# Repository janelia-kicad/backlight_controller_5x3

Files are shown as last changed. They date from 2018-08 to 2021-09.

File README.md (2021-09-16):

- [Repository Information](#orge3a2ecc)
  - [Description](#org1a124a6)
- [Images](#orgde4a8eb)
- [Schematic](#org565d04b)
- [Gerbers](#orgdefb019)
- [Bill of Materials](#orgbfc12b0)
  - [PCB Parts](#org35e0f28)
  - [Supplemental Parts](#orgb5c14fe)
  - [Vendor Parts Lists](#org5ae73cf)
- [Supplemental Documentation](#orgd3afd80)
  - [Assembly Instructions](#orgc67ada5)
- [Manufacturing Archive](#org51454f0)

# Repository Information

-   **Name:** backlight\_controller\_5x3
-   **Version:** 1.3
-   **License:** Open-Source Hardware
-   **URL:** <https://github.com/janelia-kicad/backlight_controller_5x3>
-   **Author:** Peter Polidoro
-   **Email:** peter@polidoro.io

## Description

This board controls up to four Smart Vision backlights with IR and visible channels plus additional high and low power channel outputs.

# Images

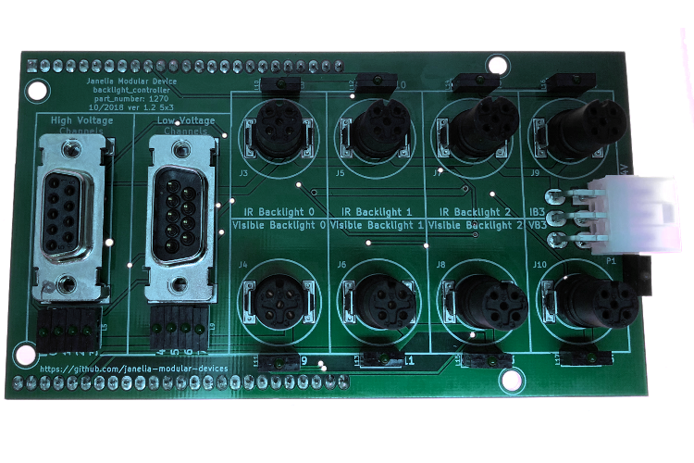
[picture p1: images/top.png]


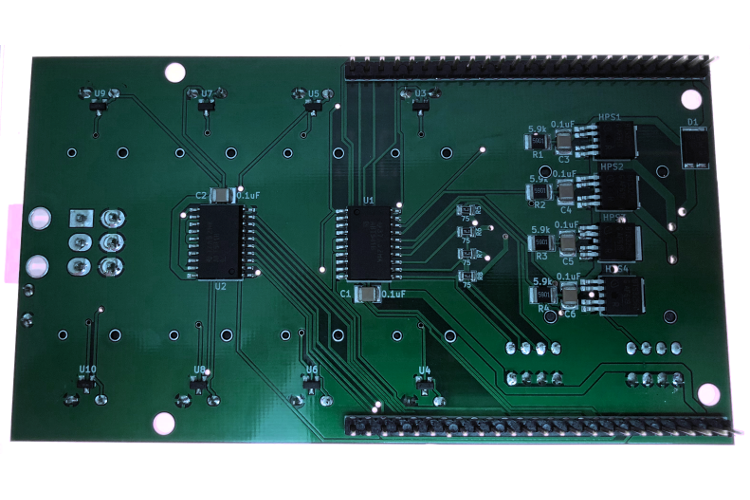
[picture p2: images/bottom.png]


# Schematic

[./schematic/backlight\_controller\_5x3.pdf](./schematic/backlight_controller_5x3.pdf)

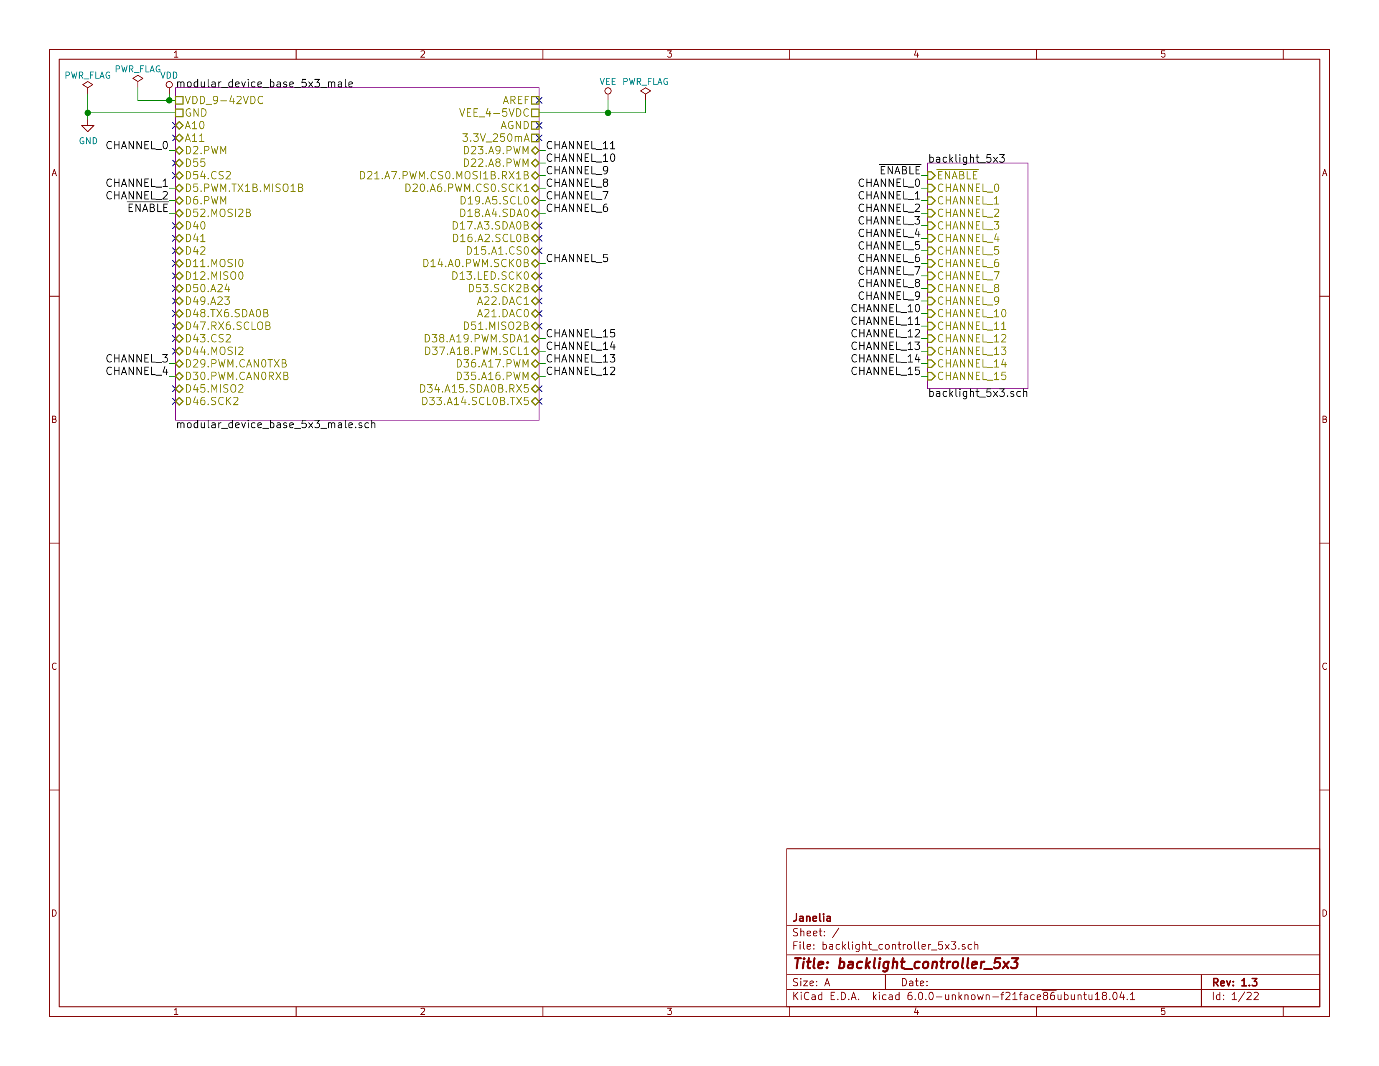
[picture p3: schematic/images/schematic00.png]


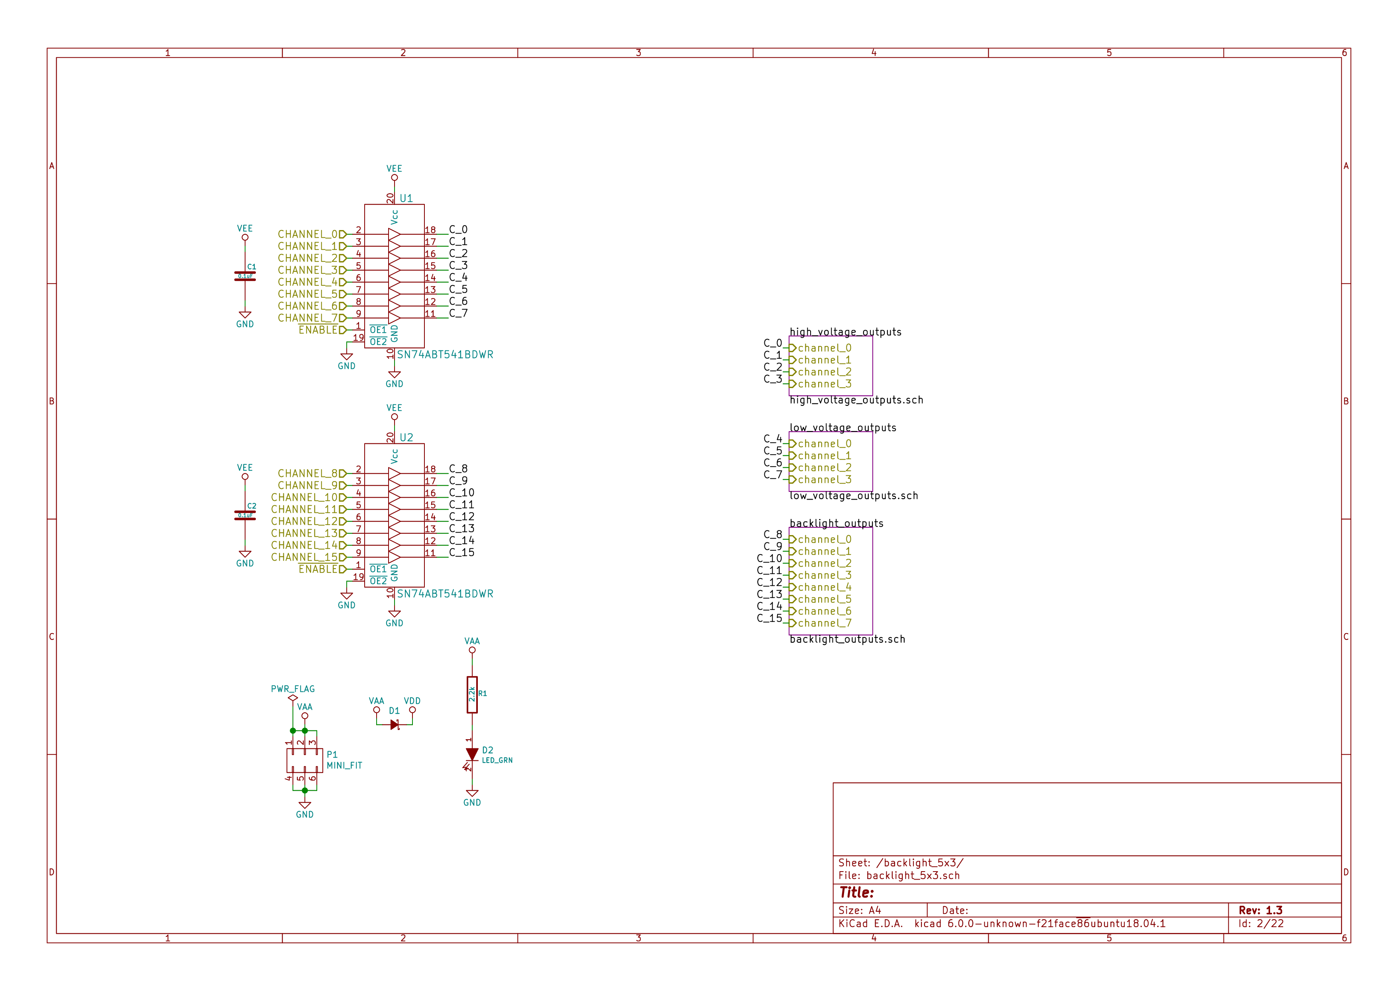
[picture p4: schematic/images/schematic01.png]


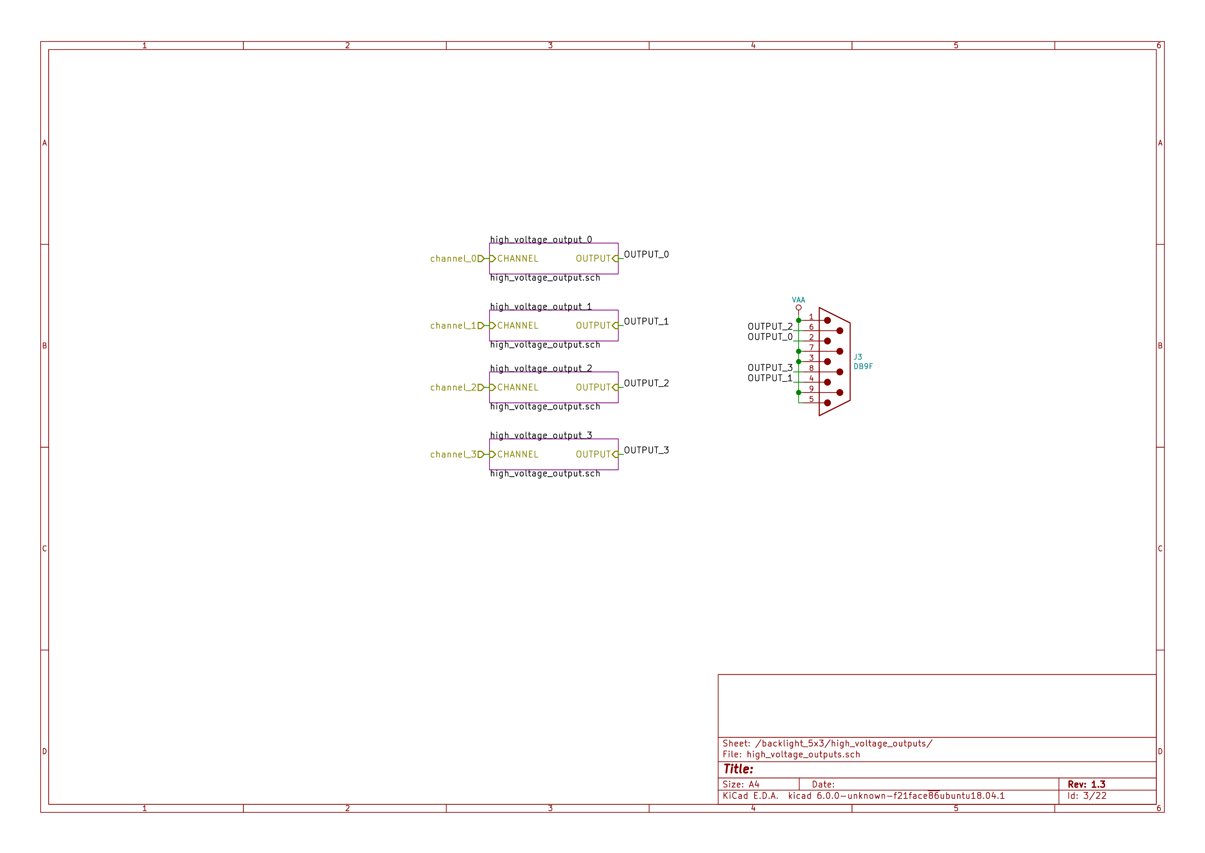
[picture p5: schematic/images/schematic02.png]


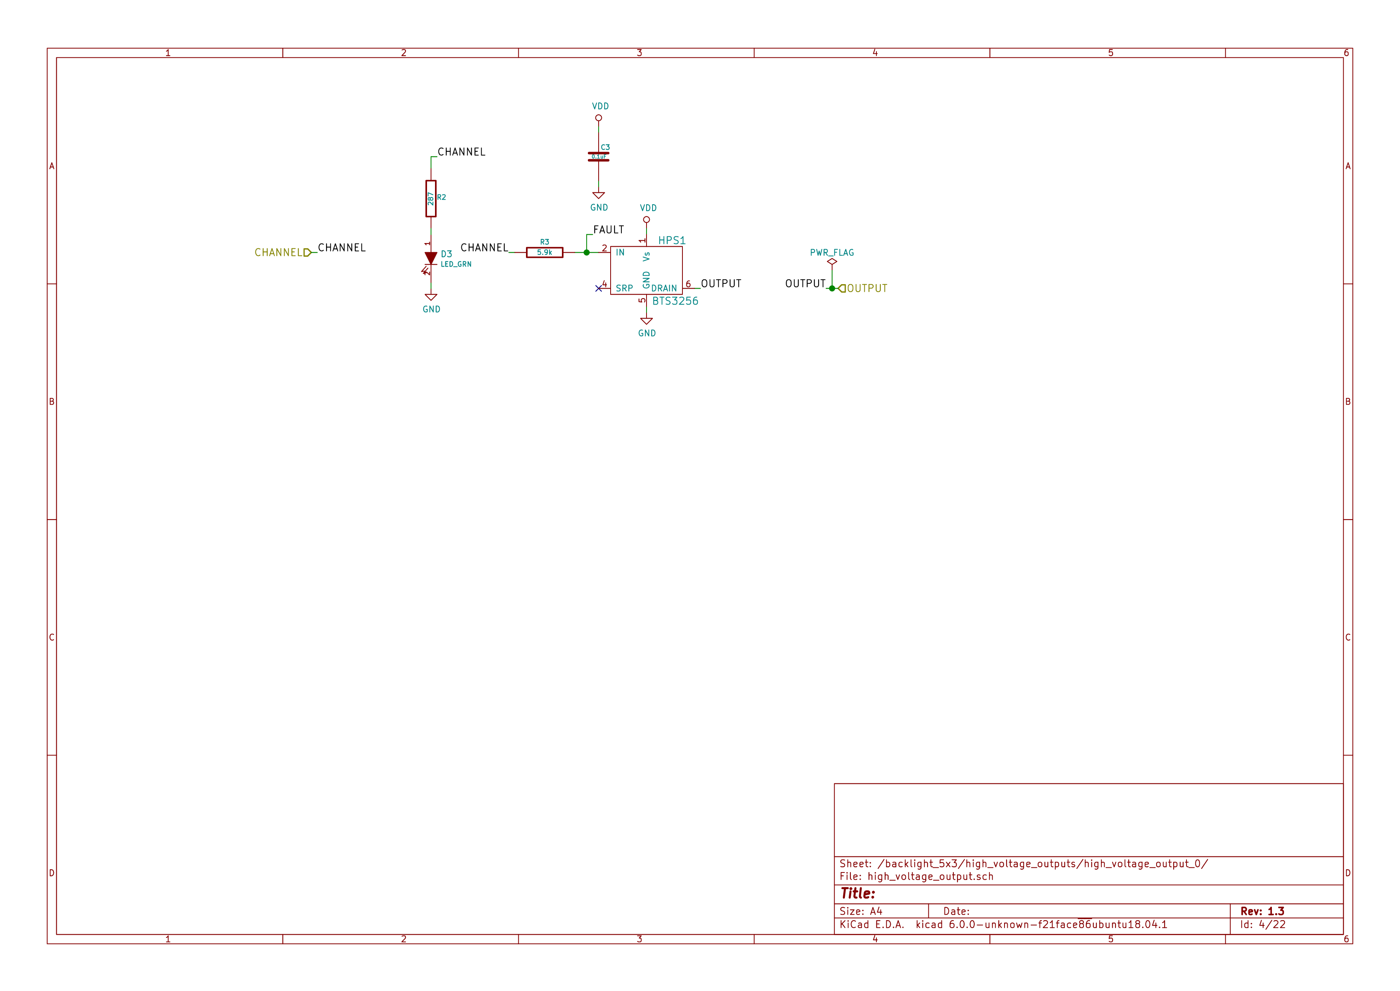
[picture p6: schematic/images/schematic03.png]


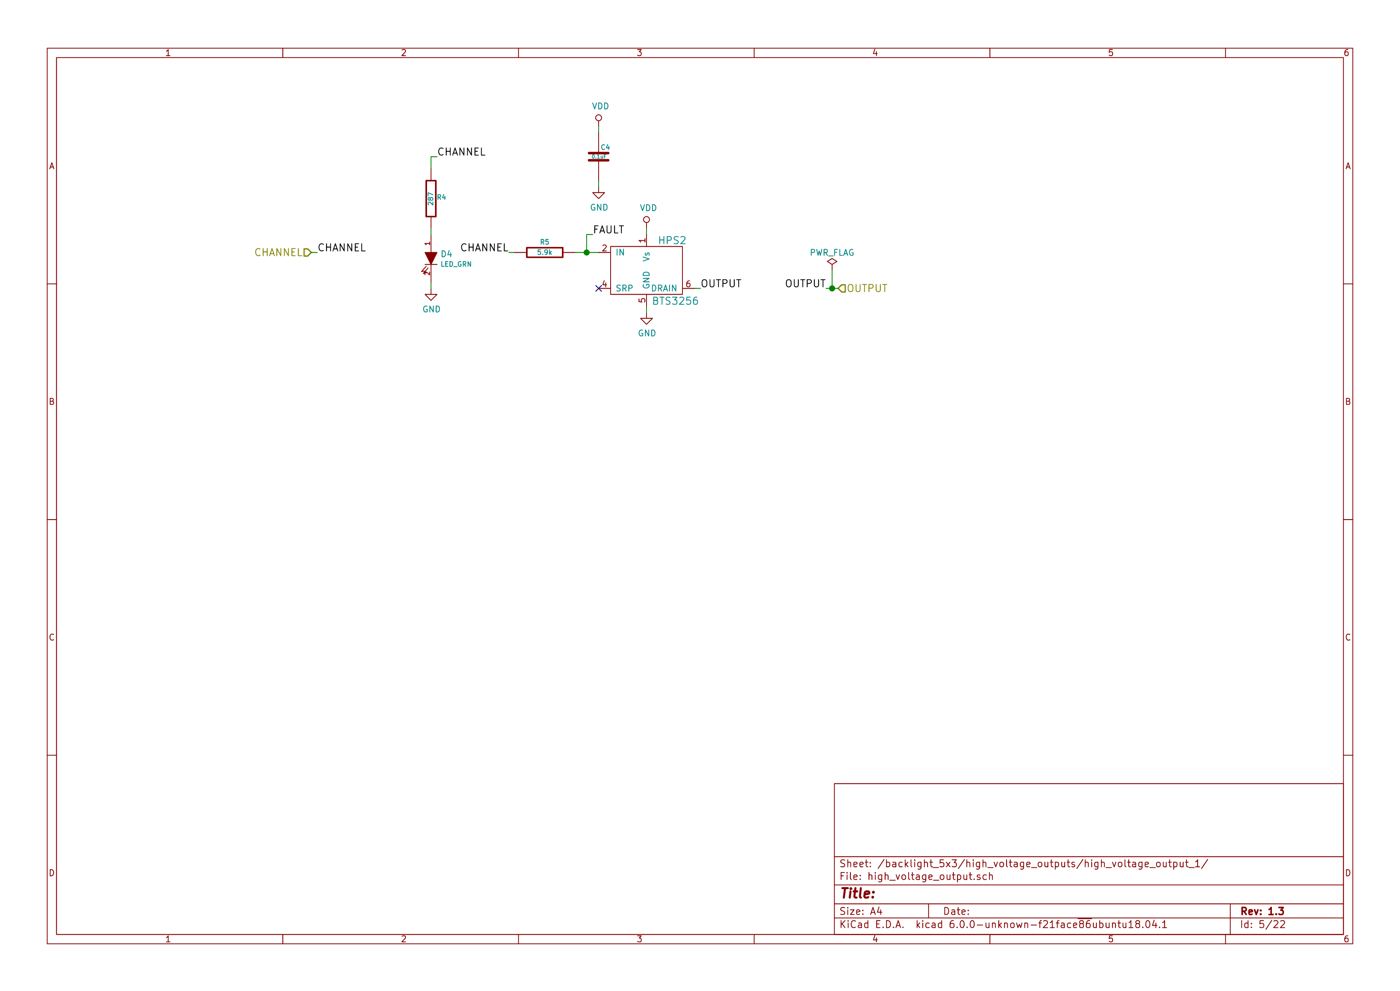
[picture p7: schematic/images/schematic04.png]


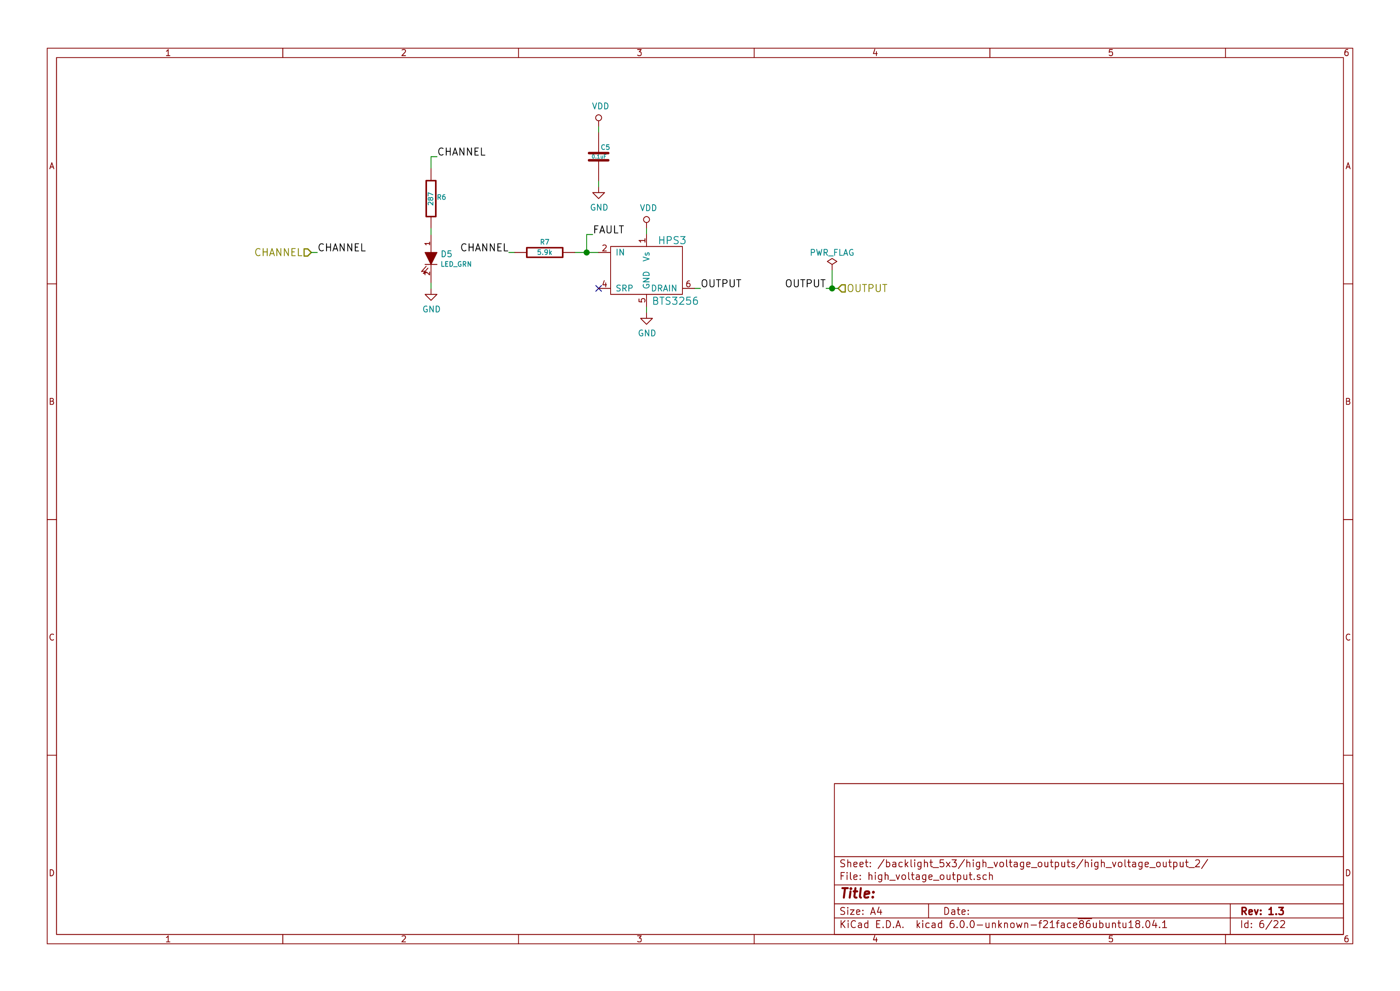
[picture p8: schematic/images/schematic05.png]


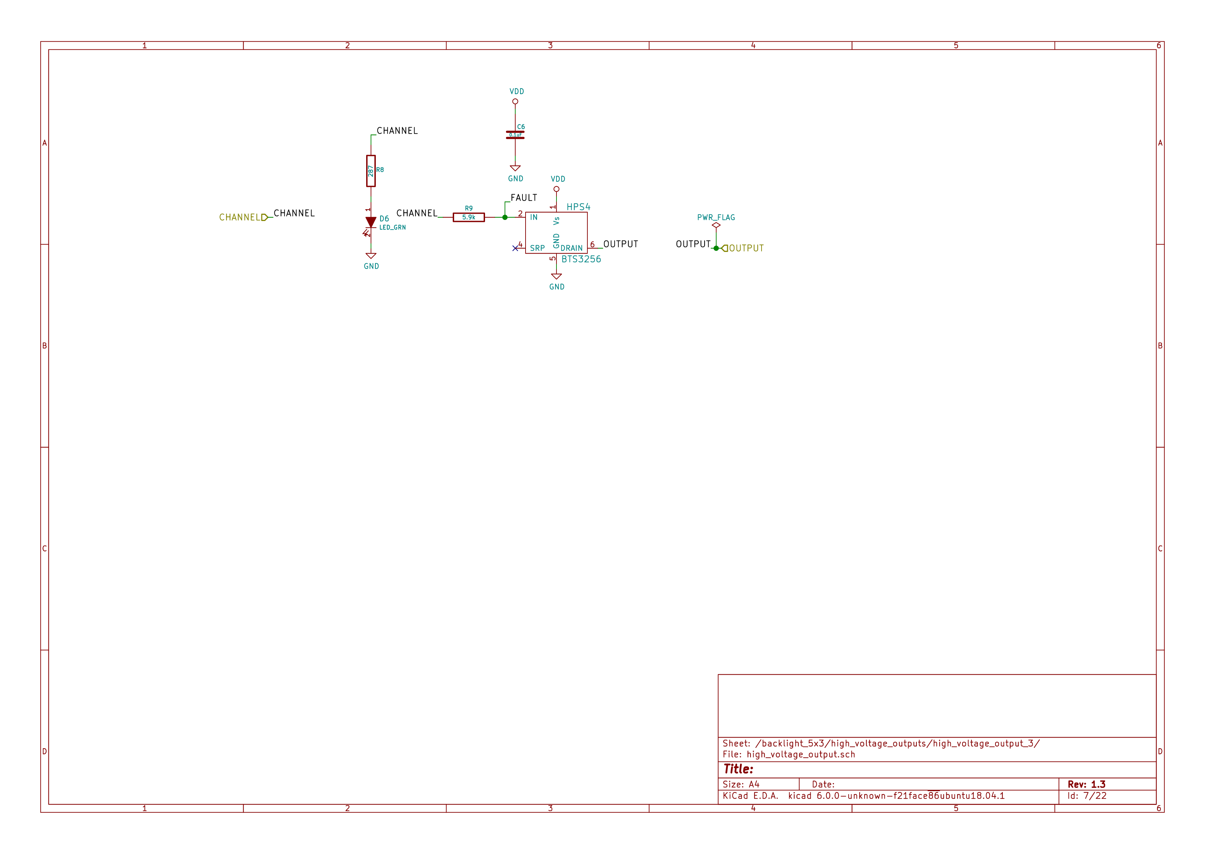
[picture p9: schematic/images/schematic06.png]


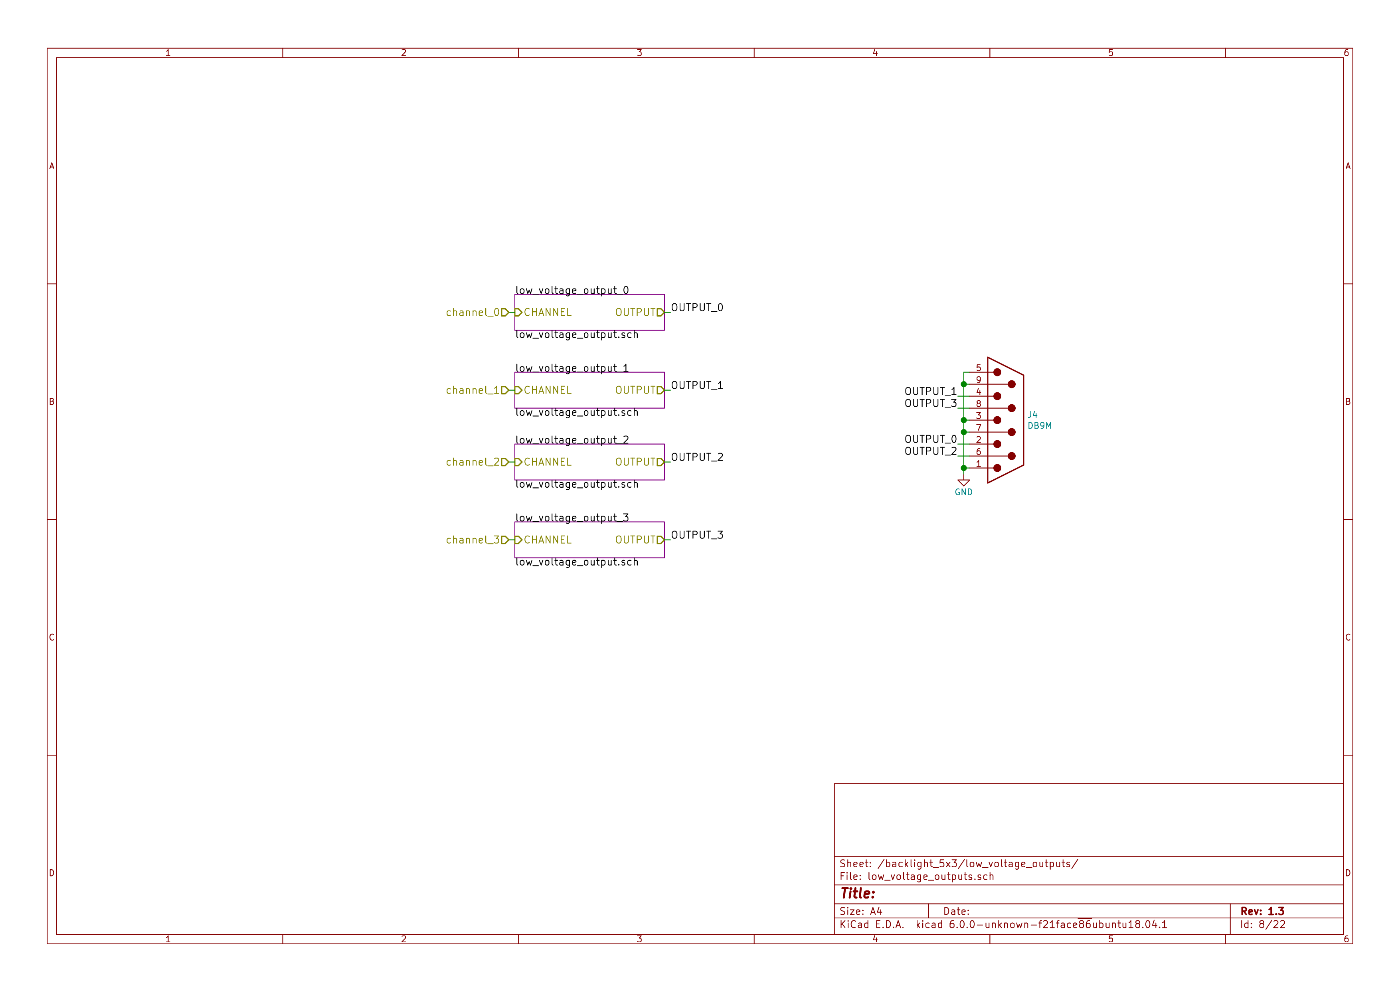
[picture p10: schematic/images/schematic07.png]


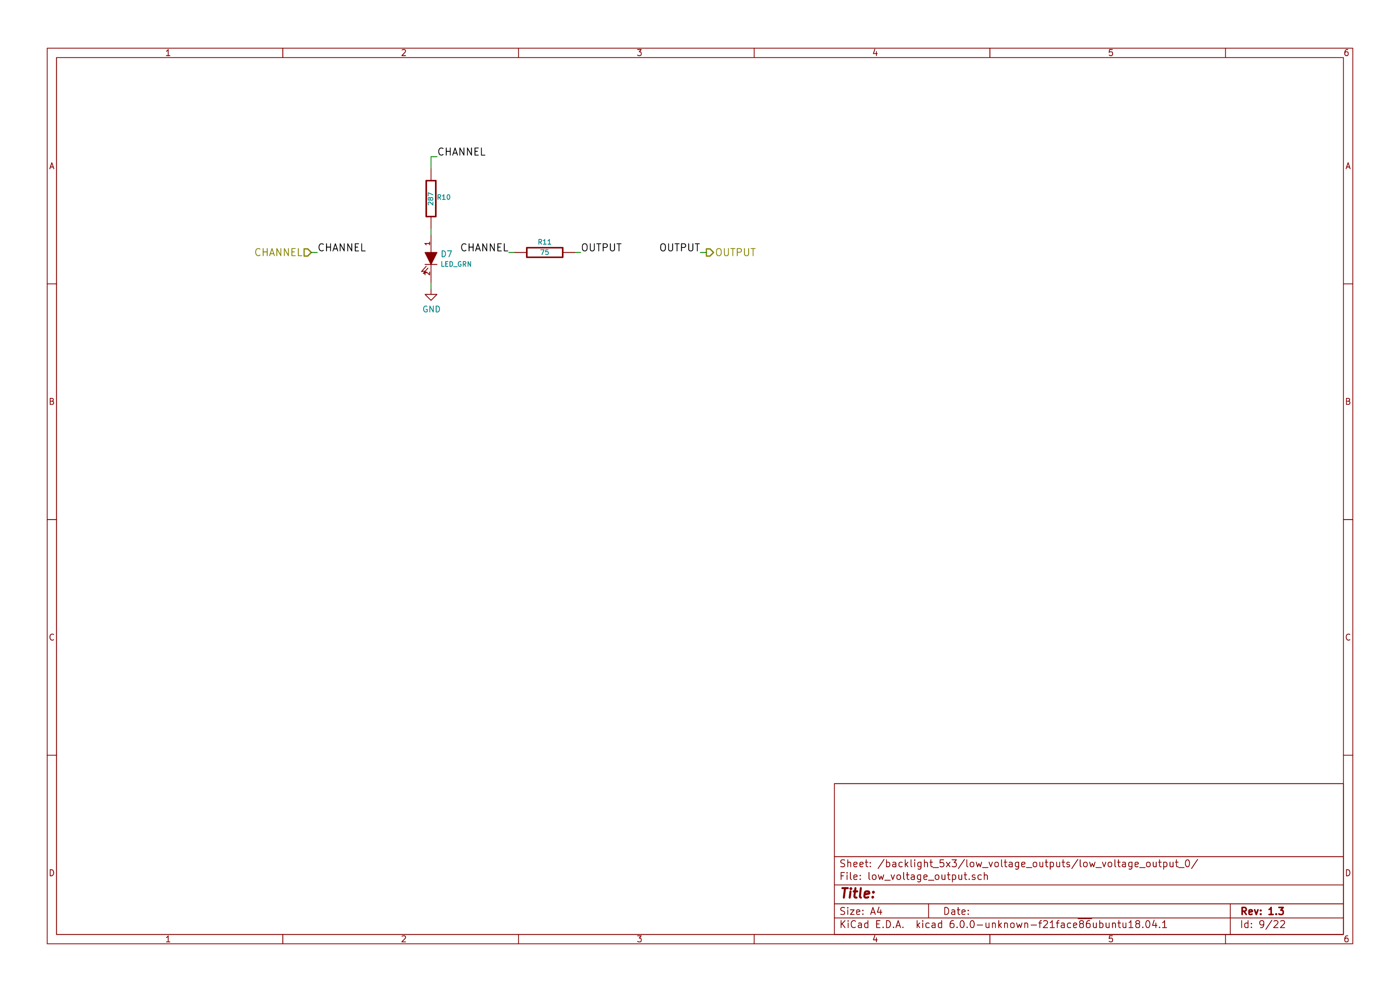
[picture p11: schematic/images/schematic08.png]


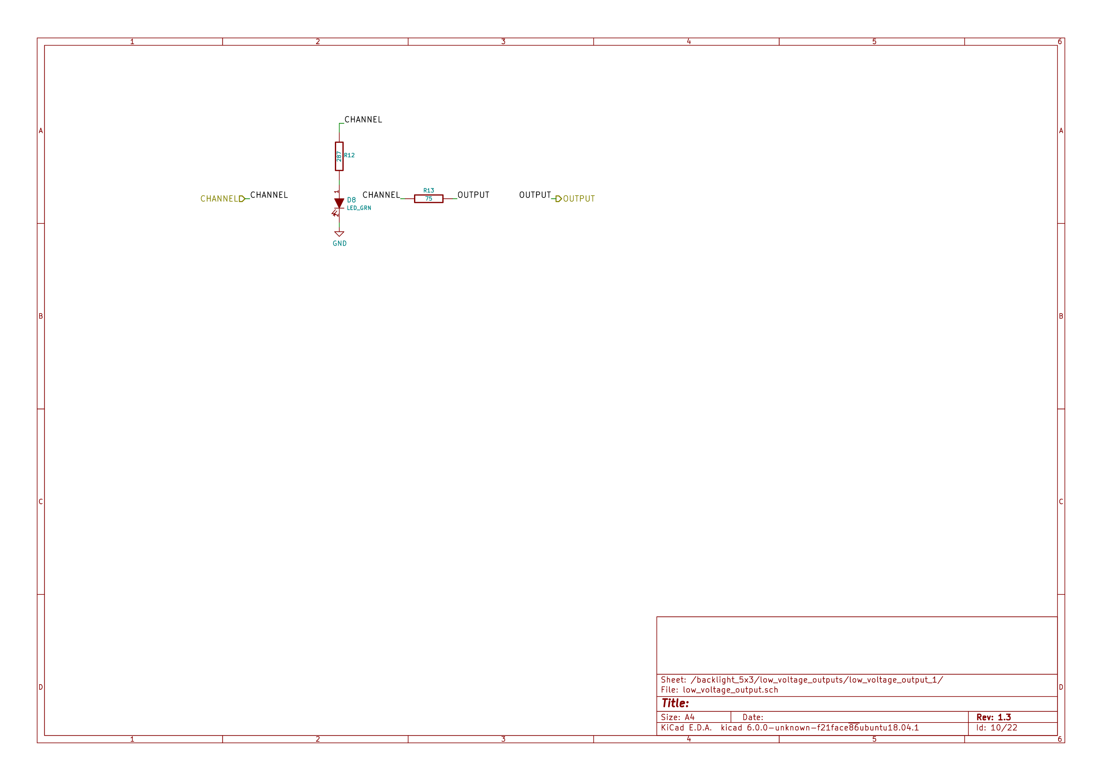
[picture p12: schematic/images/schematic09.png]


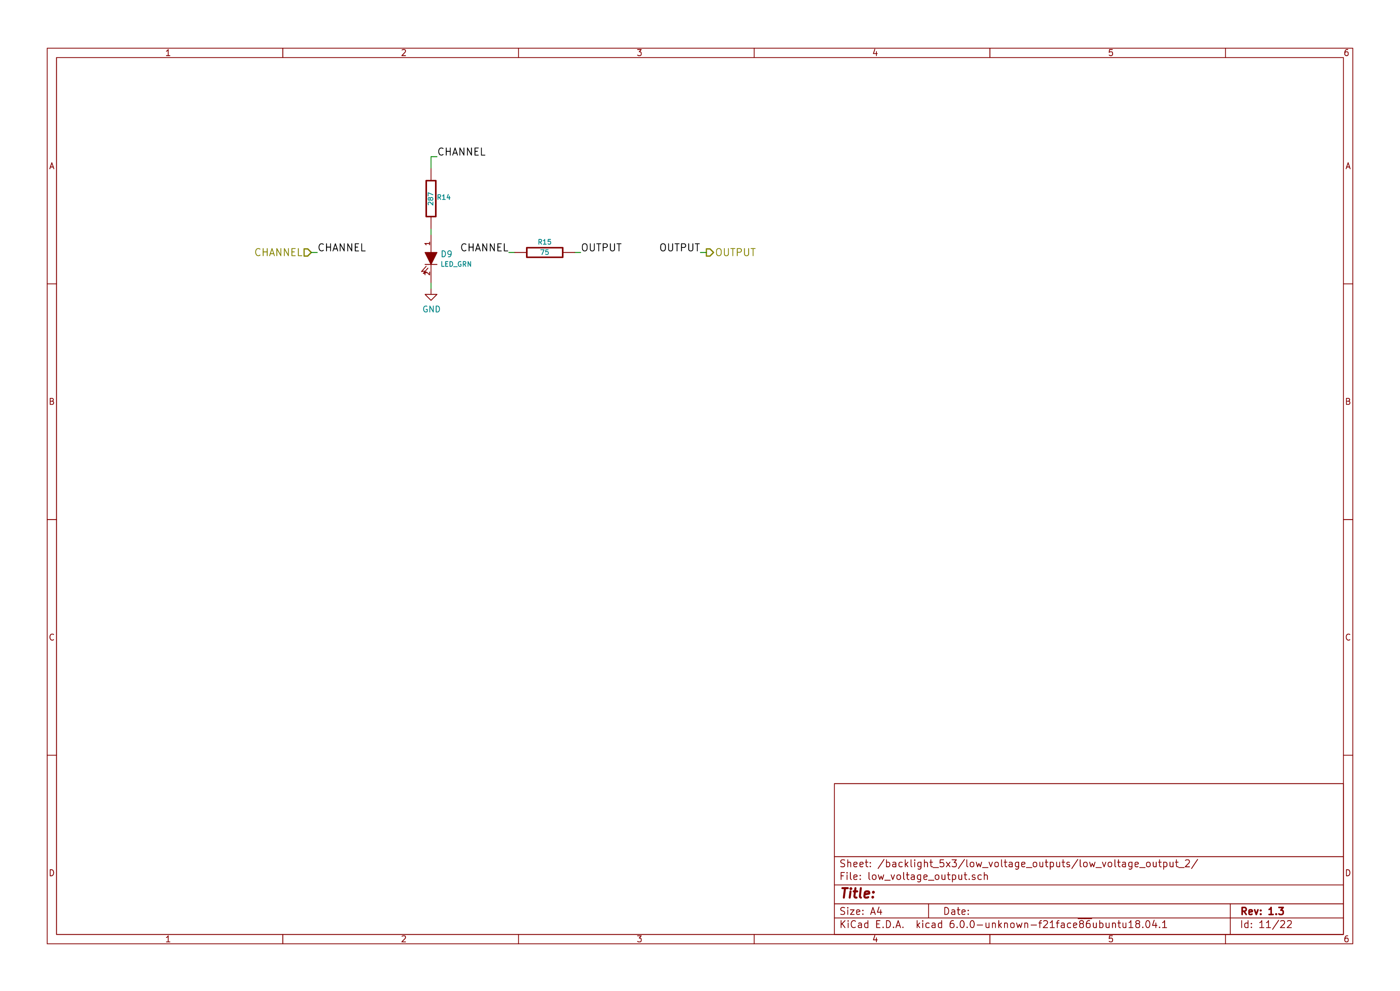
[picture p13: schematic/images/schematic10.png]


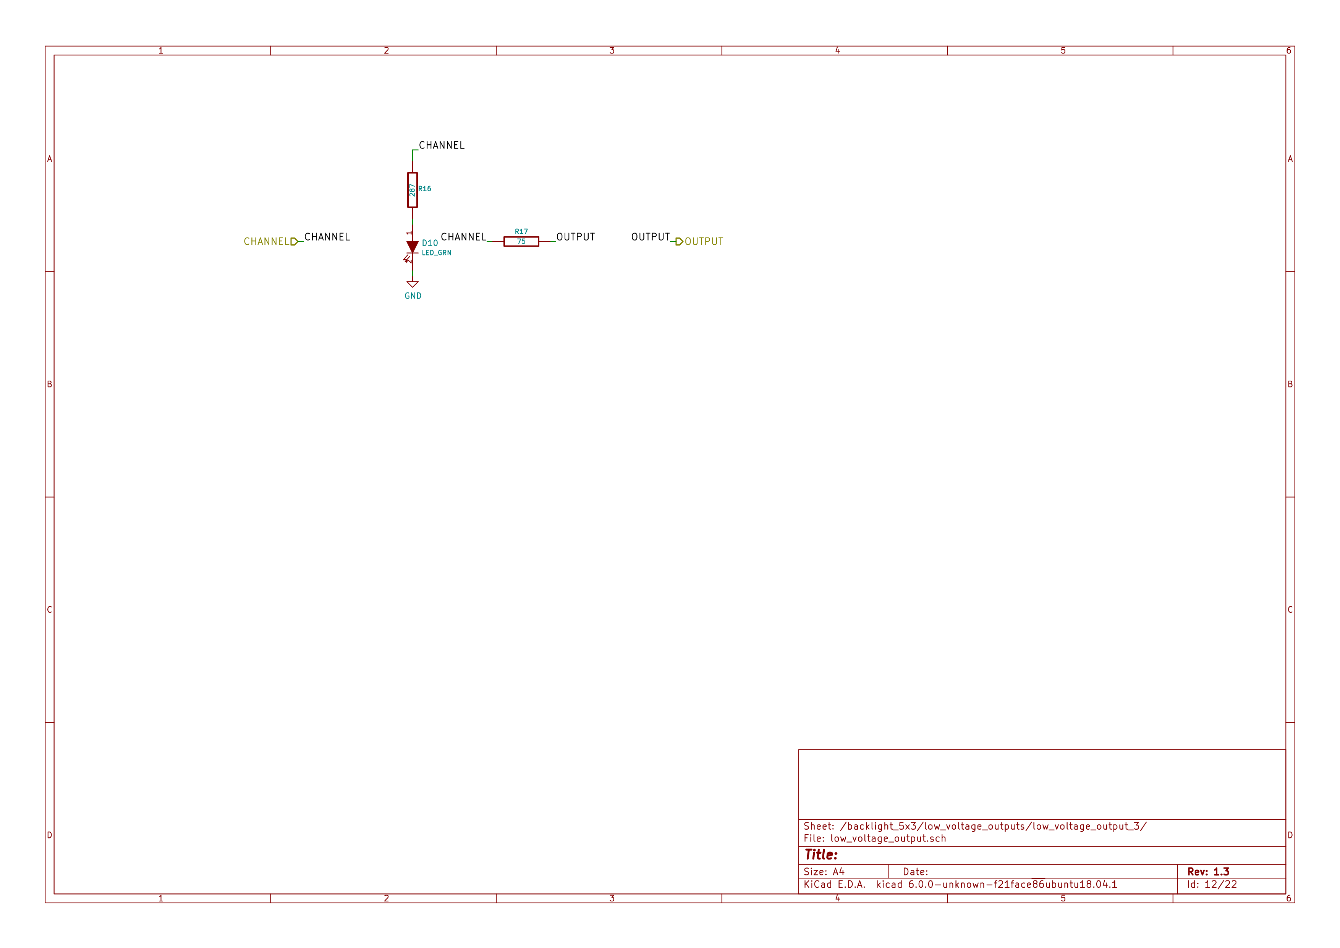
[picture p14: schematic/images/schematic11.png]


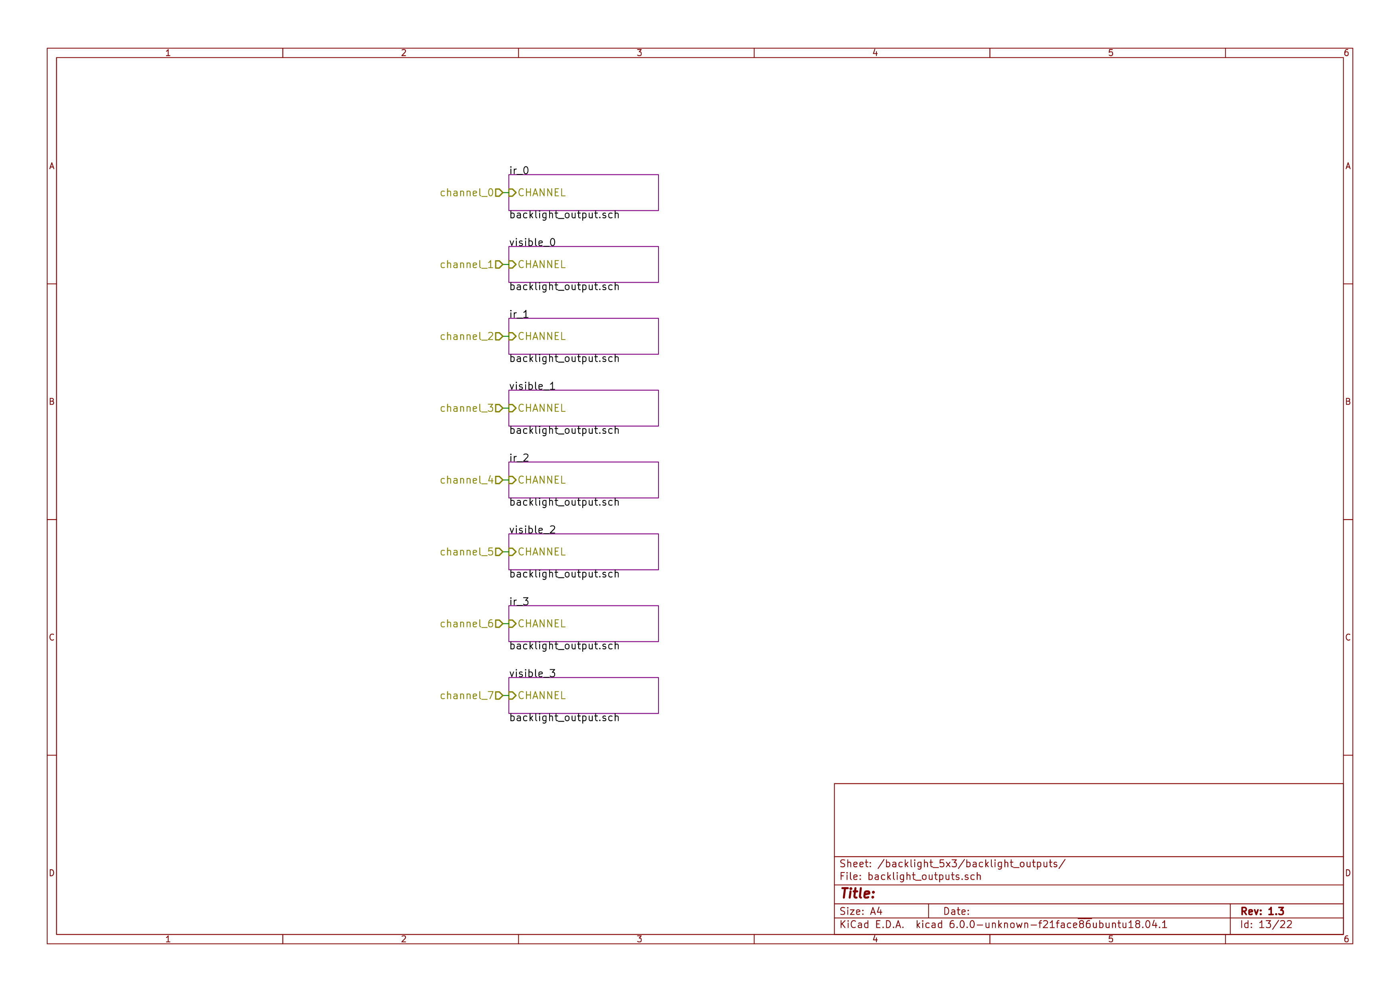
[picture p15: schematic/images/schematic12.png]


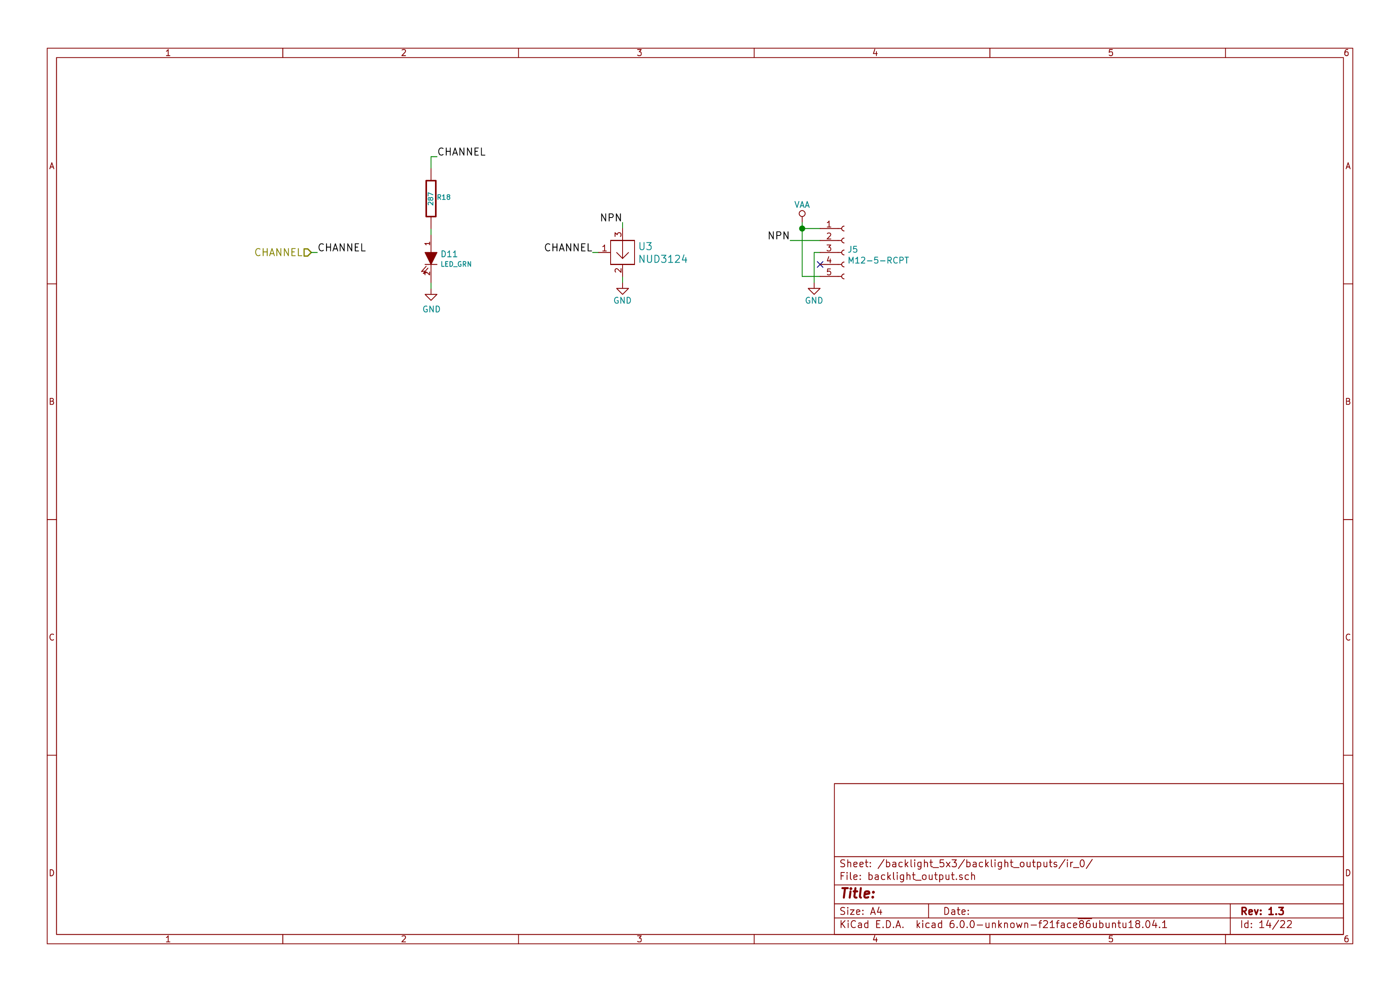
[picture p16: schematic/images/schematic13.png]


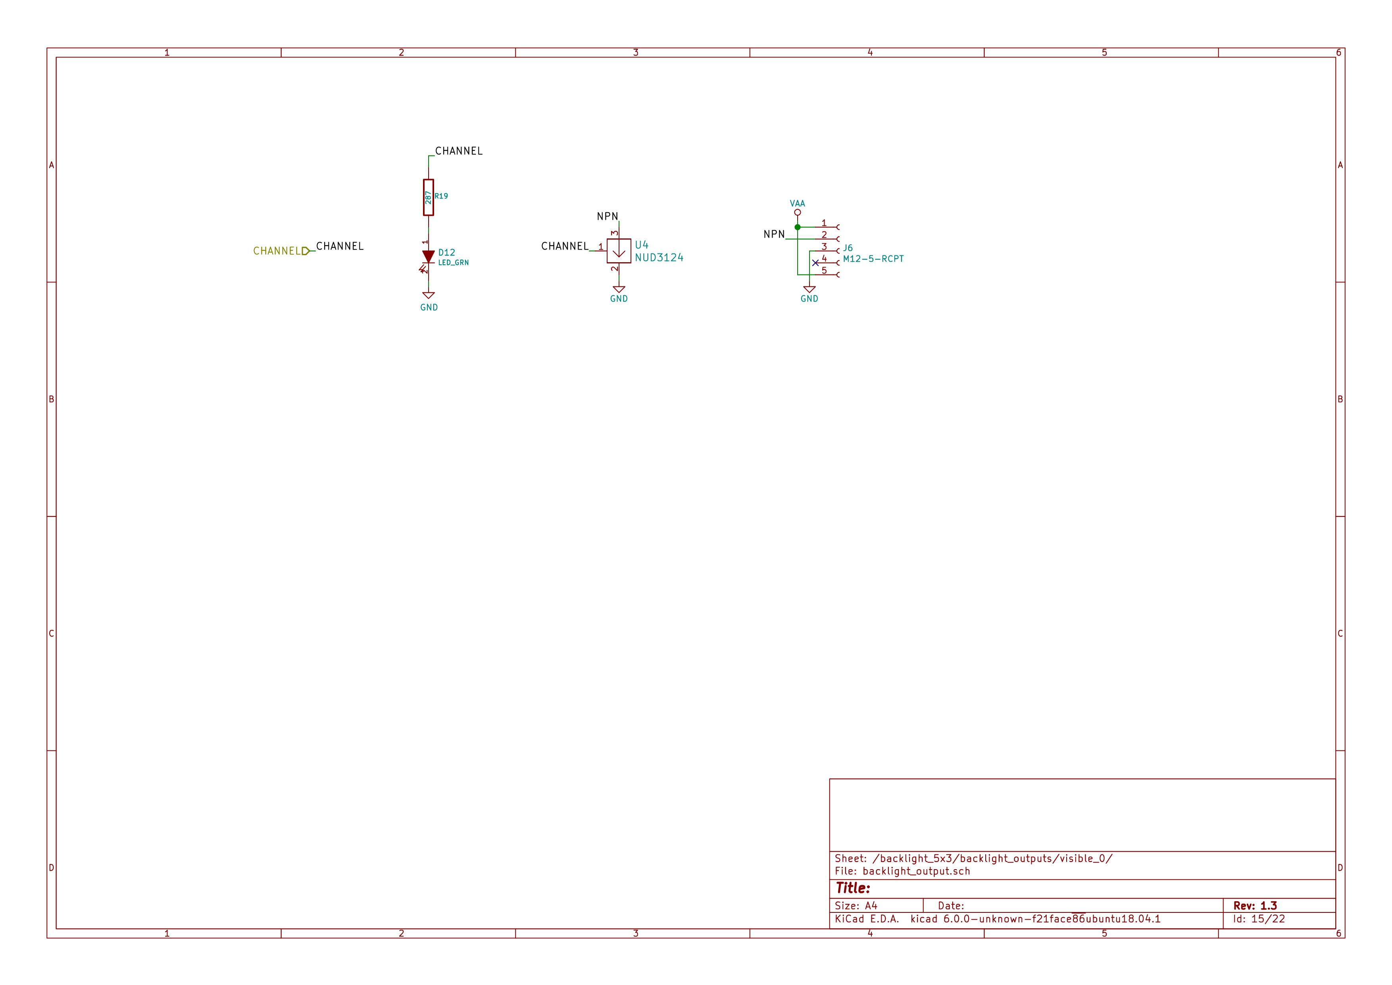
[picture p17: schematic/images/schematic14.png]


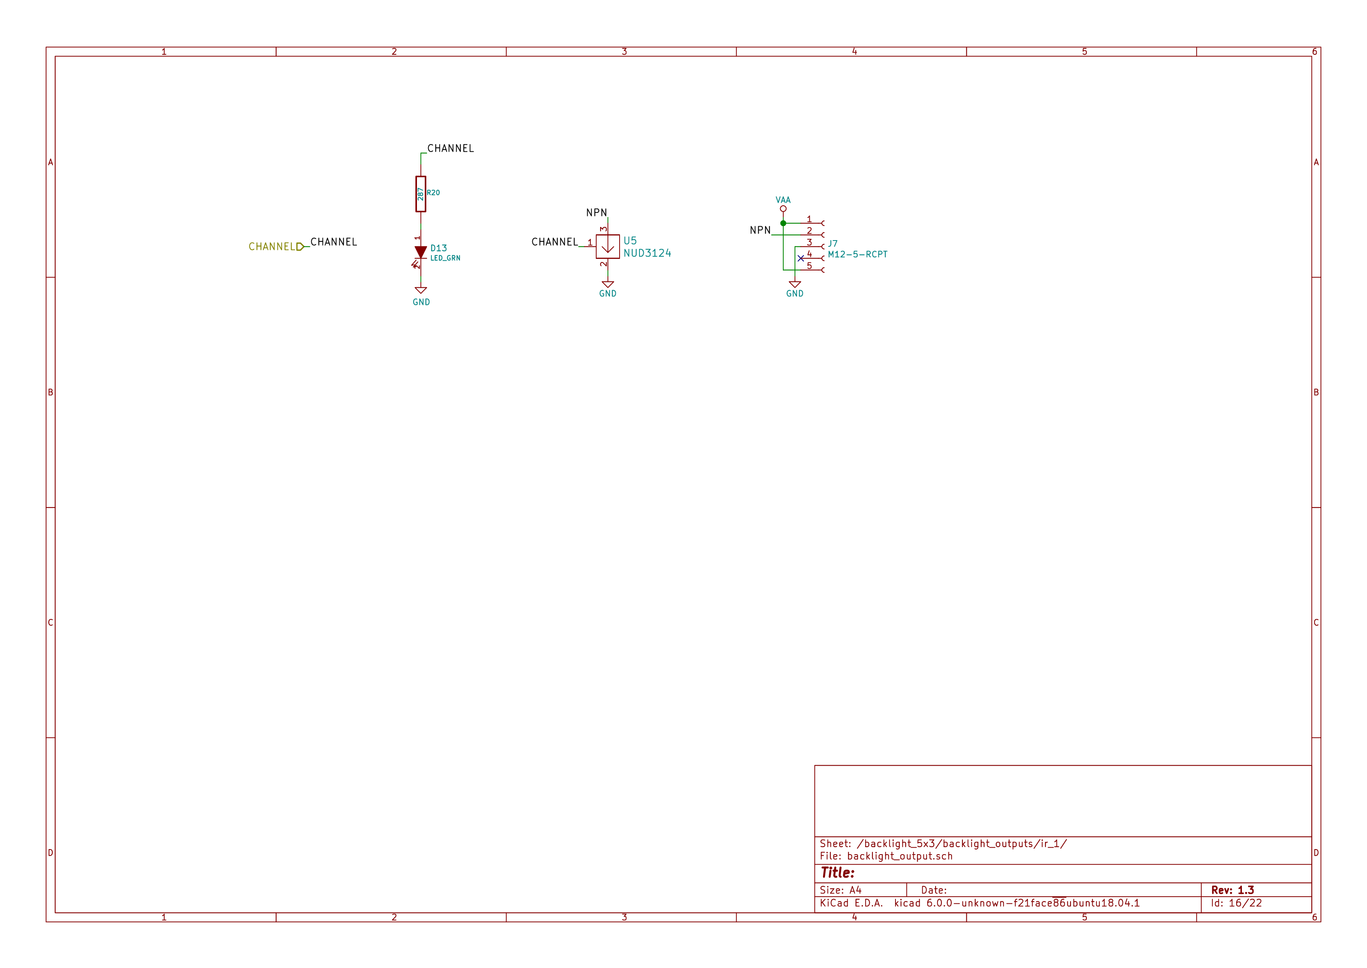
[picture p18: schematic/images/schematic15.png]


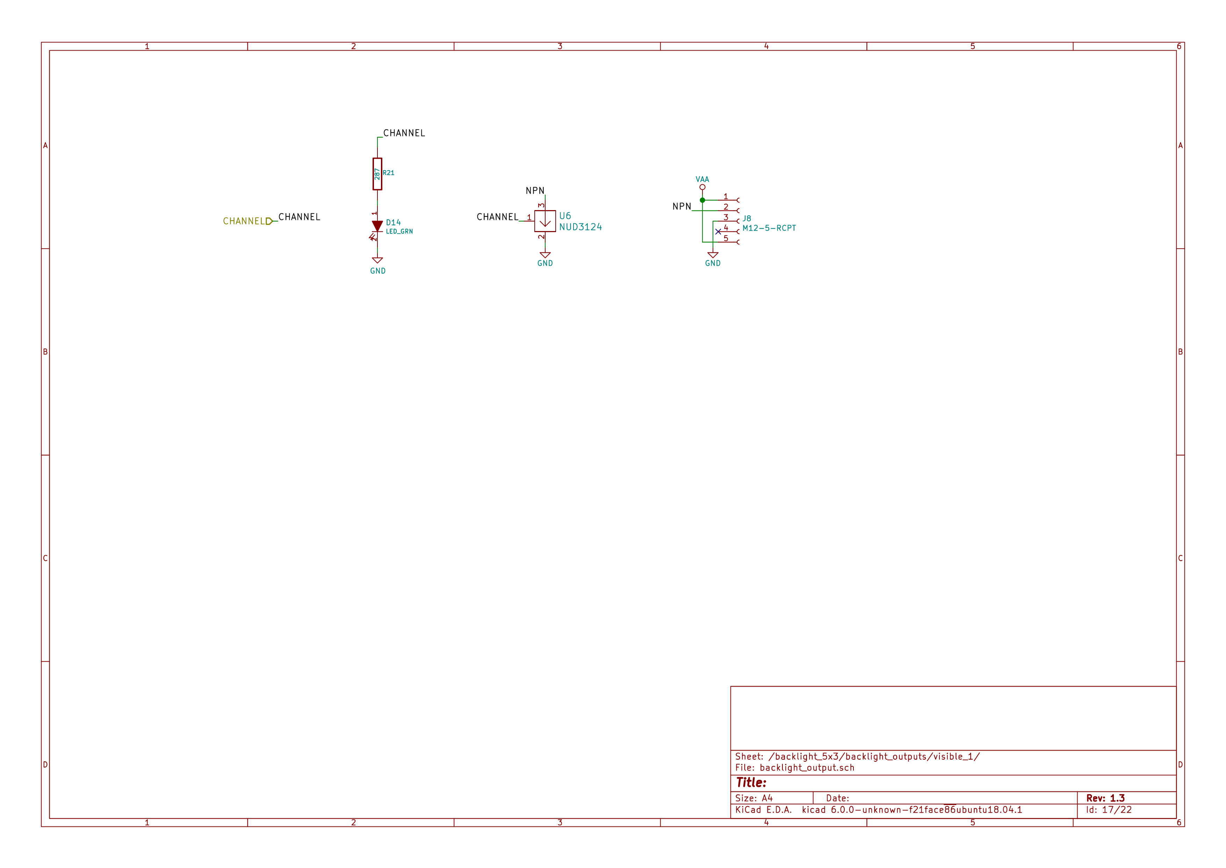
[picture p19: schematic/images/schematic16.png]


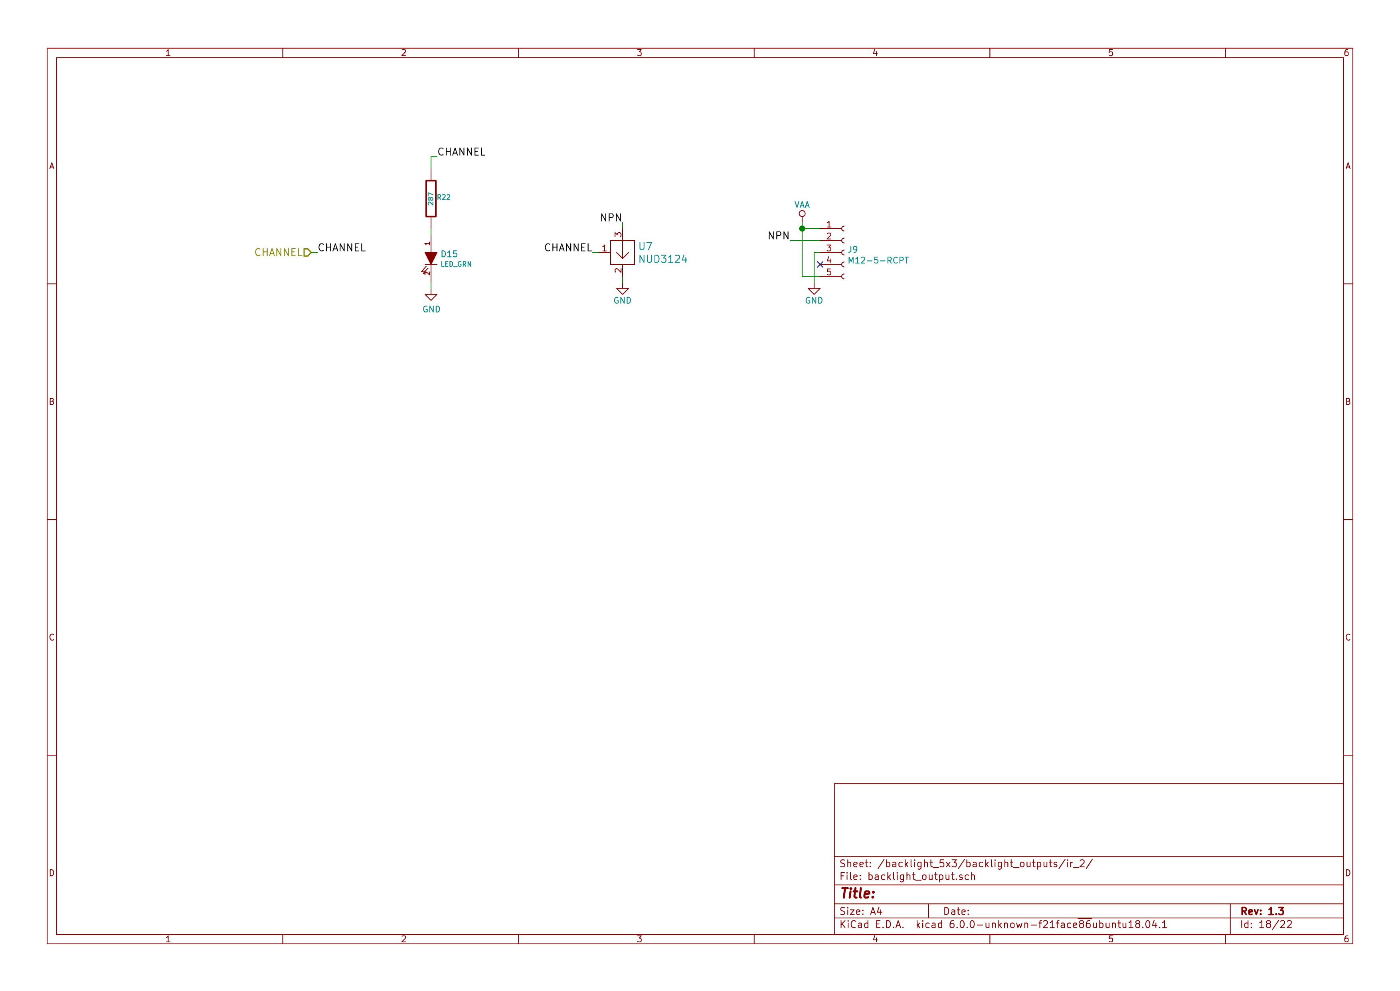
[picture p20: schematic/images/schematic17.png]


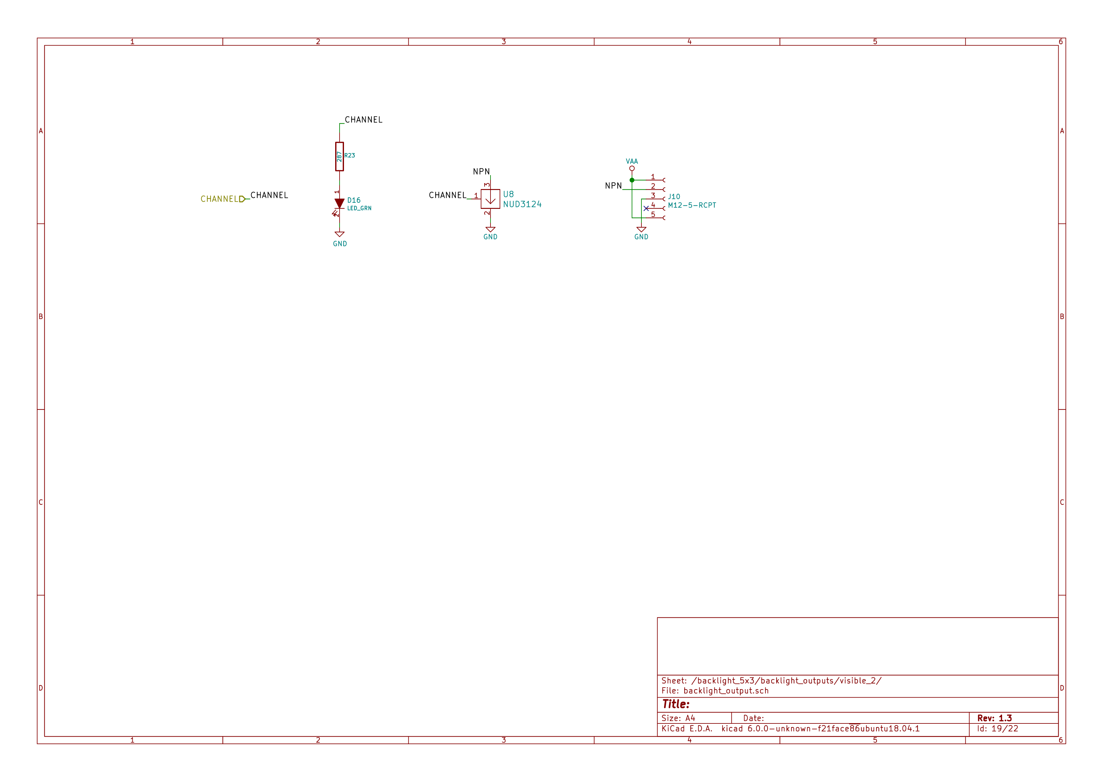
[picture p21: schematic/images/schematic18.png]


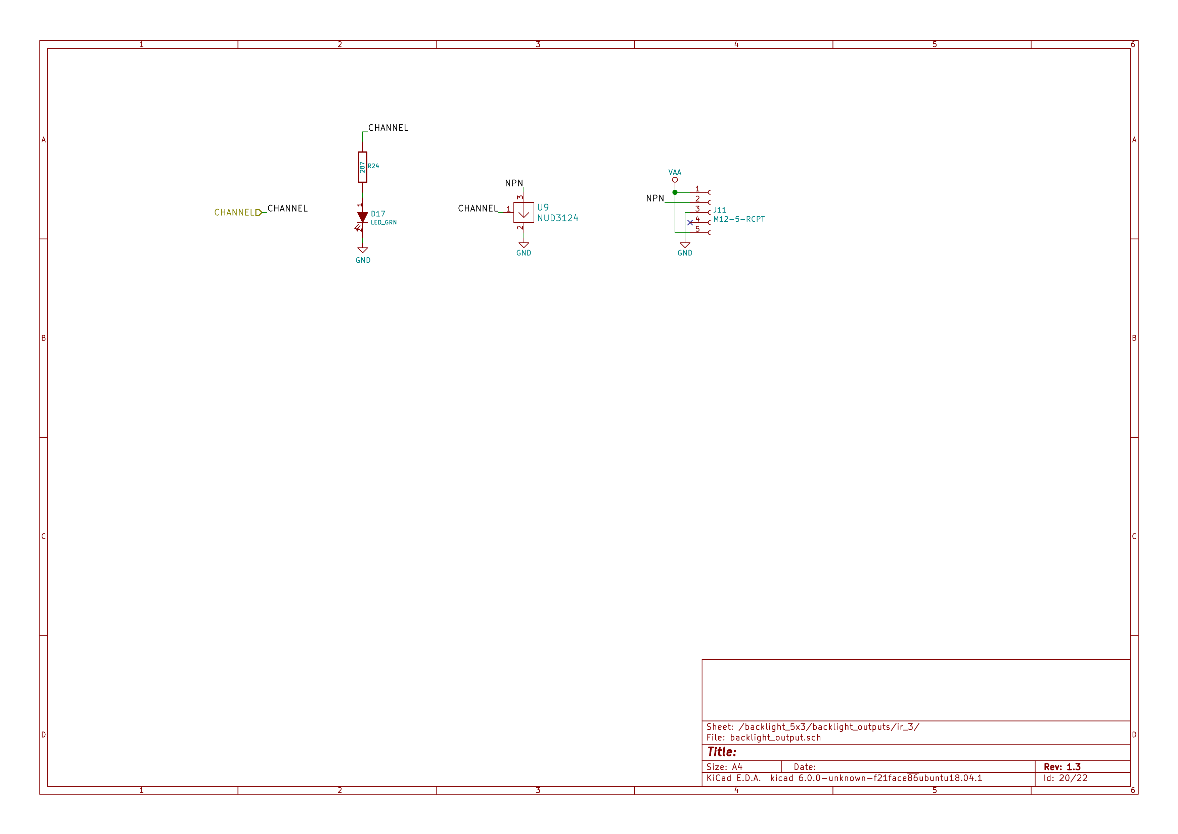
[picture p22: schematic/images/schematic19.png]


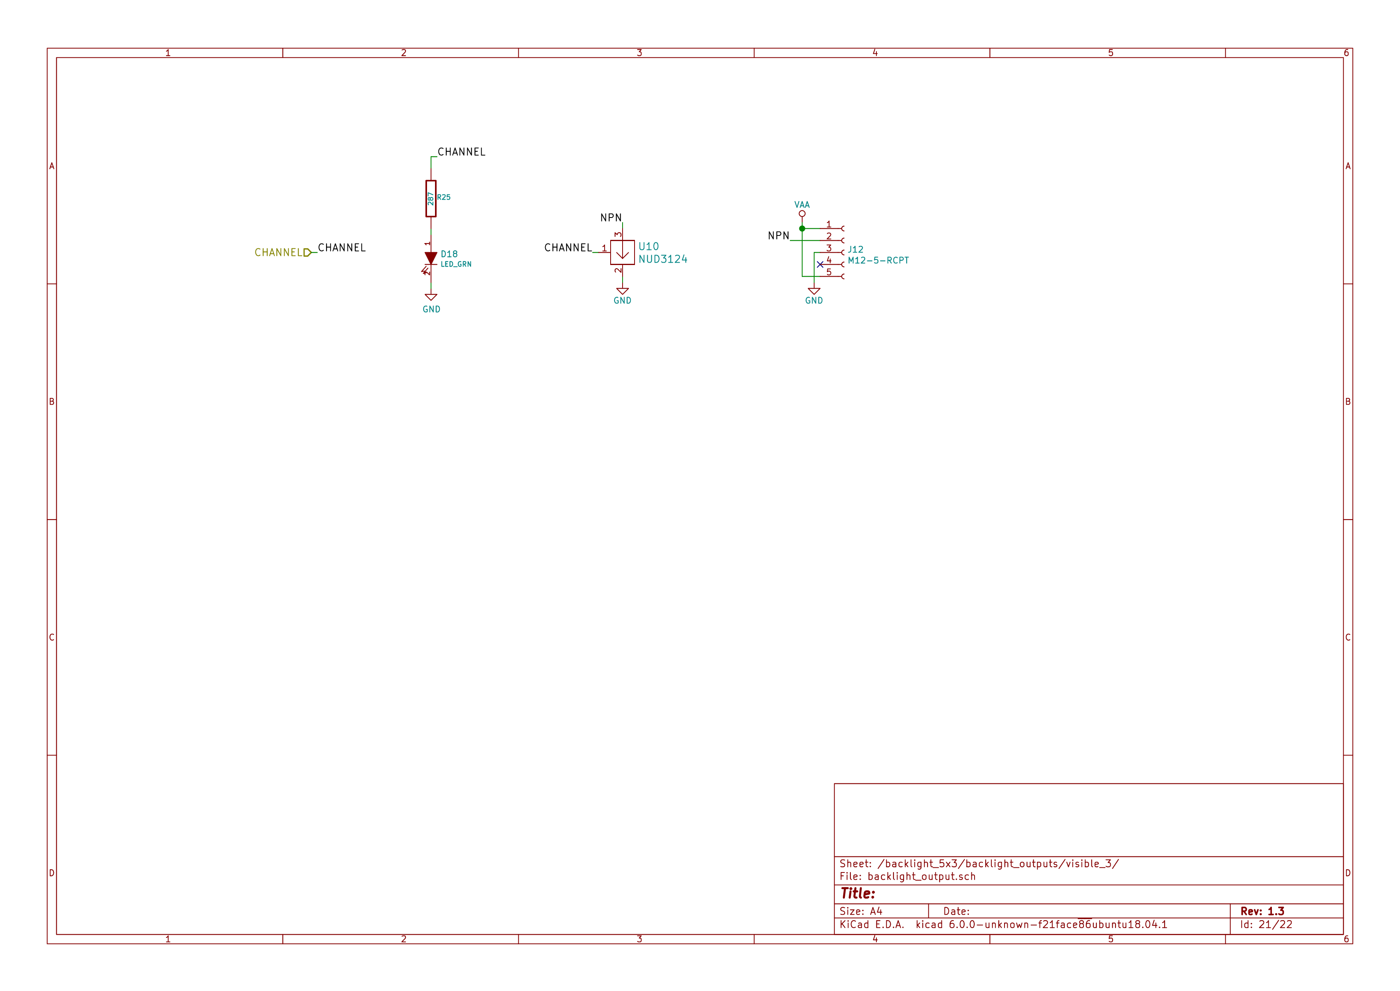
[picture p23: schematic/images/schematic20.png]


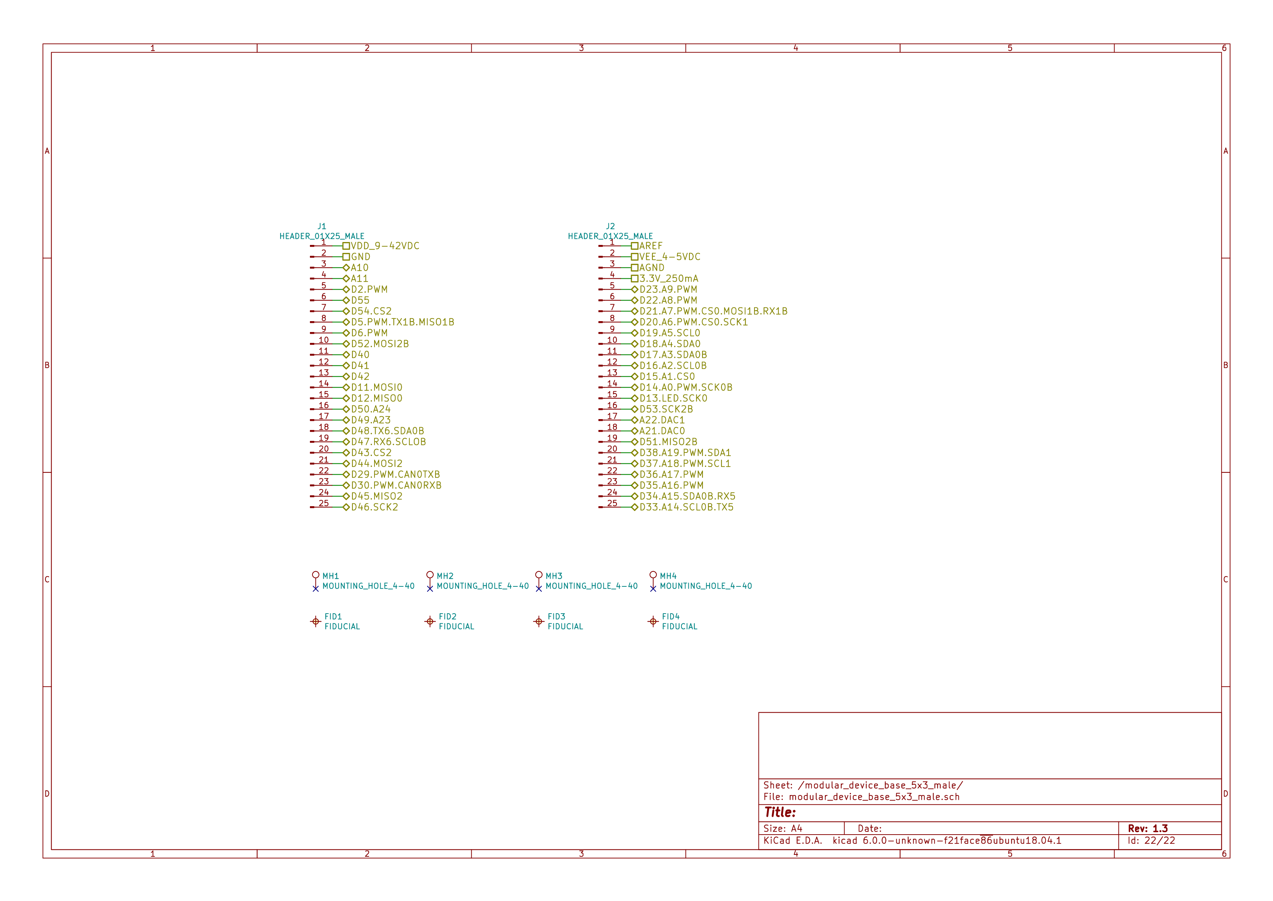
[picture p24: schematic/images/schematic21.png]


# Gerbers

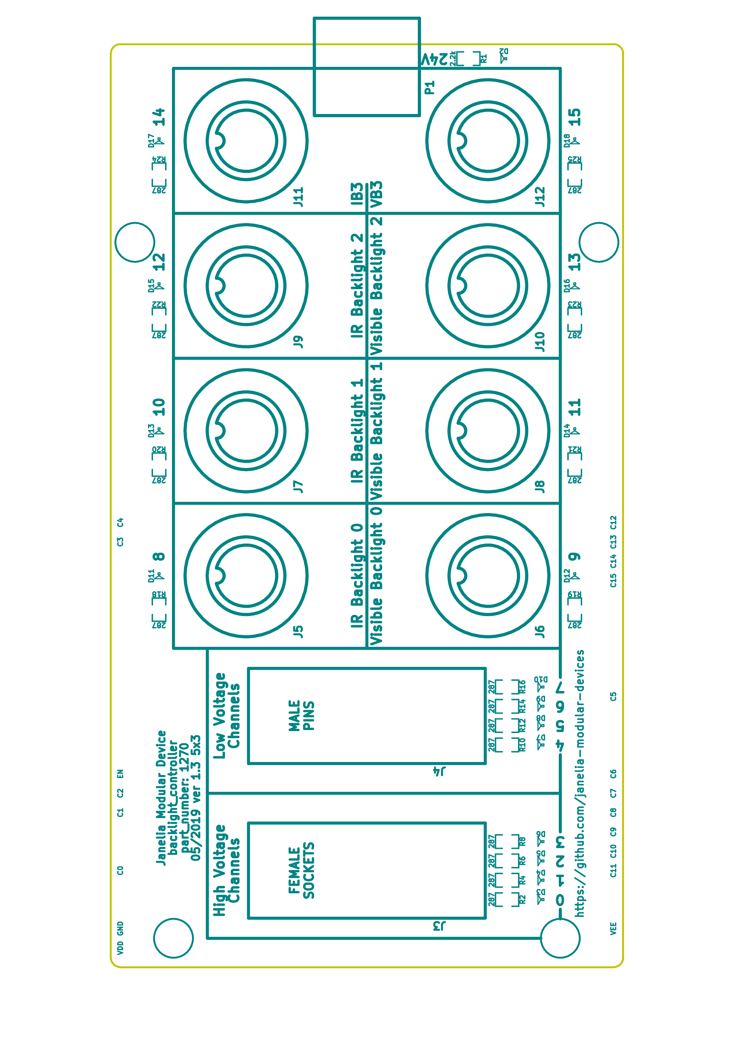
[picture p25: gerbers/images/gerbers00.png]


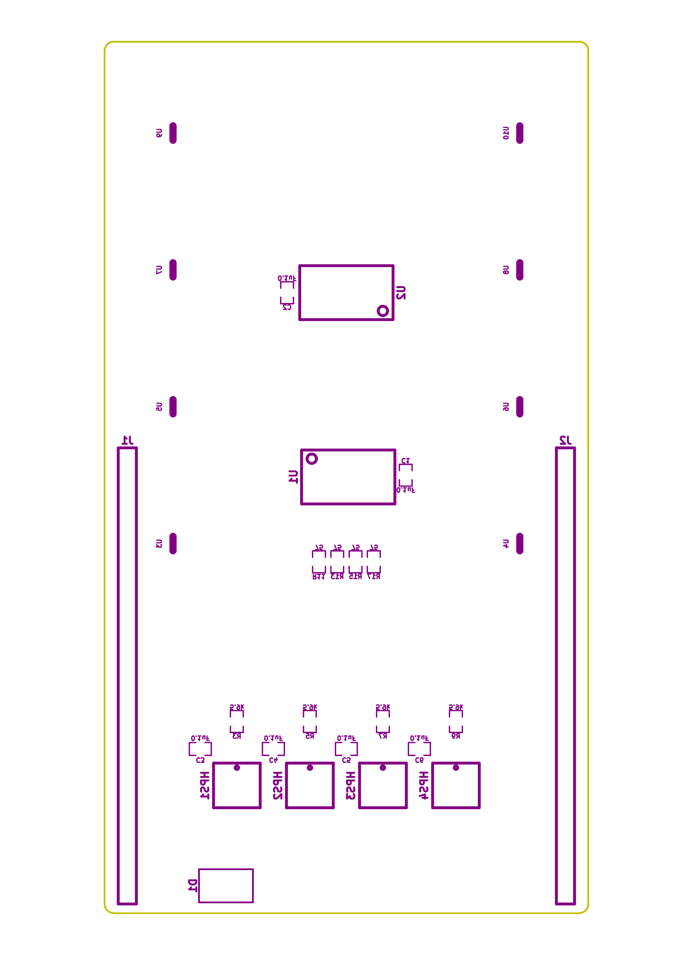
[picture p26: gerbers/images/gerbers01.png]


# Bill of Materials

## PCB Parts

| Item | Reference(s)                                                | Quantity | Manufacturer Part Number | Description                                                       |
|---- |----------------------------------------------------------- |-------- |------------------------ |----------------------------------------------------------------- |
| 1    | C1 C2 C3 C4 C5 C6                                           | 6        | C0805T104K5RAL7800       | CAP CER 0.1UF 50V X7R                                             |
| 2    | D1                                                          | 1        | PMEG045V100EPDZ          | DIODE SCHOTTKY 45V 10A                                            |
| 3    | D10 D11 D12 D13 D14 D15 D16 D17 D18 D2 D3 D4 D5 D6 D7 D8 D9 | 17       | LTST-C170GKT             | LED GREEN CLEAR SMD                                               |
| 4    | HPS1 HPS2 HPS3 HPS4                                         | 4        | BTS3256DAUMA1            | IC SWITCH SMART LOWSIDE                                           |
| 5    | J1 J2                                                       | 2        | PBC25SAAN                | CONN HEADER VERT 25POS 2.54MM                                     |
| 6    | J10 J11 J12 J5 J6 J7 J8 J9                                  | 8        | 1411976                  | CONN FMALE INSERT 5POS SOLDER                                     |
| 7    | J3                                                          | 1        | 09551156612741           | CONN D-SUB RCPT 9POS SMD SOLDER                                   |
| 8    | J4                                                          | 1        | 09551296812741           | CONN D-SUB PLUG 9POS SMD SOLDER                                   |
| 9    | P1                                                          | 1        | 0039301060               | CONN HEADER 6POS 4.2MM R/A TIN                                    |
| 10   | R1                                                          | 1        | ERJ-6ENF2201V            | RES SMD 2.2K OHM 1% 1/8W                                          |
| 11   | R10 R12 R14 R16 R18 R19 R2 R20 R21 R22 R23 R24 R25 R4 R6 R8 | 16       | ERJ-6ENF2870V            | RES SMD 287 OHM 1% 1/8W                                           |
| 12   | R11 R13 R15 R17                                             | 4        | ERJ-6ENF75R0V            | RES SMD 75 OHM 1% 1/8W                                            |
| 13   | R3 R5 R7 R9                                                 | 4        | ERJ-6ENF5901V            | RES SMD 5.9K OHM 1% 1/8W                                          |
| 14   | U1 U2                                                       | 2        | SN74ABT541BDWR           | Buffer Non-Inverting 1 Element 8 Bit per Element Push-Pull Output |
| 15   | U10 U3 U4 U5 U6 U7 U8 U9                                    | 8        | NUD3124LT1G              | IC INDCT LOAD DRVR AUTO                                           |

## Supplemental Parts

| Item | Quantity | Manufacturer Part Number   | Description                    |
|---- |-------- |-------------------------- |------------------------------ |
| 1    | 1        | GST280A24-C6P              | AC/DC DESKTOP ADAPTER 24V 280W |
| 2    | 1        | CORD IEC 320-C13 6FT BLACK | CORD IEC 320-C13 6FT BLACK     |

## Vendor Parts Lists

[./bom/Digi-Key\_parts.csv](./bom/Digi-Key_parts.csv)

[./bom/supplemental\_Digi-Key\_parts.csv](./bom/supplemental_Digi-Key_parts.csv)

# Supplemental Documentation

## Assembly Instructions

-   Solder surface mount and through hole components onto the pcb.

# Manufacturing Archive

Send manufacturing zip file to your favorite PCB manufacturer for fabrication.

[./manufacturing/backlight\_controller\_5x3\_v1.3.zip](./manufacturing/backlight_controller_5x3_v1.3.zip)

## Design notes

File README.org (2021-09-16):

# Created 2019-05-20 Mon 15:17
#+OPTIONS: title:nil author:nil email:nil toc:t |:t ^:nil
* Repository Information

- Name :: backlight_controller_5x3
- Version :: 1.3
- License :: Open-Source Hardware
- URL :: https://github.com/janelia-kicad/backlight_controller_5x3
- Author :: Peter Polidoro
- Email :: peter@polidoro.io

** Description

This board controls up to four Smart Vision backlights with IR and visible
channels plus additional high and low power channel outputs.

* Images





* Schematic

[[file:./schematic/backlight_controller_5x3.pdf][./schematic/backlight_controller_5x3.pdf]]













































* Gerbers





* Bill of Materials

** PCB Parts

| Item | Reference(s)                                                | Quantity | Manufacturer Part Number | Description                                                       |
|------+-------------------------------------------------------------+----------+--------------------------+-------------------------------------------------------------------|
|    1 | C1 C2 C3 C4 C5 C6                                           |        6 | C0805T104K5RAL7800       | CAP CER 0.1UF 50V X7R                                             |
|    2 | D1                                                          |        1 | PMEG045V100EPDZ          | DIODE SCHOTTKY 45V 10A                                            |
|    3 | D10 D11 D12 D13 D14 D15 D16 D17 D18 D2 D3 D4 D5 D6 D7 D8 D9 |       17 | LTST-C170GKT             | LED GREEN CLEAR SMD                                               |
|    4 | HPS1 HPS2 HPS3 HPS4                                         |        4 | BTS3256DAUMA1            | IC SWITCH SMART LOWSIDE                                           |
|    5 | J1 J2                                                       |        2 | PBC25SAAN                | CONN HEADER VERT 25POS 2.54MM                                     |
|    6 | J10 J11 J12 J5 J6 J7 J8 J9                                  |        8 | 1411976                  | CONN FMALE INSERT 5POS SOLDER                                     |
|    7 | J3                                                          |        1 | 09551156612741           | CONN D-SUB RCPT 9POS SMD SOLDER                                   |
|    8 | J4                                                          |        1 | 09551296812741           | CONN D-SUB PLUG 9POS SMD SOLDER                                   |
|    9 | P1                                                          |        1 | 0039301060               | CONN HEADER 6POS 4.2MM R/A TIN                                    |
|   10 | R1                                                          |        1 | ERJ-6ENF2201V            | RES SMD 2.2K OHM 1% 1/8W                                          |
|   11 | R10 R12 R14 R16 R18 R19 R2 R20 R21 R22 R23 R24 R25 R4 R6 R8 |       16 | ERJ-6ENF2870V            | RES SMD 287 OHM 1% 1/8W                                           |
|   12 | R11 R13 R15 R17                                             |        4 | ERJ-6ENF75R0V            | RES SMD 75 OHM 1% 1/8W                                            |
|   13 | R3 R5 R7 R9                                                 |        4 | ERJ-6ENF5901V            | RES SMD 5.9K OHM 1% 1/8W                                          |
|   14 | U1 U2                                                       |        2 | SN74ABT541BDWR           | Buffer Non-Inverting 1 Element 8 Bit per Element Push-Pull Output |
|   15 | U10 U3 U4 U5 U6 U7 U8 U9                                    |        8 | NUD3124LT1G              | IC INDCT LOAD DRVR AUTO                                           |

** Supplemental Parts

| Item | Quantity | Manufacturer Part Number   | Description                    |
|------+----------+----------------------------+--------------------------------|
|    1 |        1 | GST280A24-C6P              | AC/DC DESKTOP ADAPTER 24V 280W |
|    2 |        1 | CORD IEC 320-C13 6FT BLACK | CORD IEC 320-C13 6FT BLACK     |

** Vendor Parts Lists

[[file:./bom/Digi-Key_parts.csv][./bom/Digi-Key_parts.csv]]

[[file:./bom/supplemental_Digi-Key_parts.csv][./bom/supplemental_Digi-Key_parts.csv]]

* Supplemental Documentation

** Assembly Instructions

- Solder surface mount and through hole components onto the pcb.

* Manufacturing Archive

Send manufacturing zip file to your favorite PCB manufacturer for fabrication.

[[file:./manufacturing/backlight_controller_5x3_v1.3.zip][./manufacturing/backlight_controller_5x3_v1.3.zip]]

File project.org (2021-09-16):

* Header                                                           :noexport:

  #+MACRO: name backlight_controller_5x3
  #+MACRO: version 1.3
  #+MACRO: license Open-Source Hardware
  #+MACRO: url https://github.com/janelia-kicad/backlight_controller_5x3
  #+AUTHOR: Peter Polidoro
  #+EMAIL: peter@polidoro.io

* Description

  This board controls up to four Smart Vision backlights with IR and visible
  channels plus additional high and low power channel outputs.

* Assembly Instructions

  - Solder surface mount and through hole components onto the pcb.

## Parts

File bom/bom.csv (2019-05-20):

Item | Reference(s) | Quantity | Manufacturer | Manufacturer Part Number | Vendor | Vendor Part Number | Description | Package
1 | C1 C2 C3 C4 C5 C6 | 6 | KEMET | C0805T104K5RAL7800 | Digi-Key | 399-14636-1-ND | CAP CER 0.1UF 50V X7R | 0805 (2012 Metric)
2 | D1 | 1 | Nexperia USA Inc. | PMEG045V100EPDZ | Digi-Key | 1727-1904-1-ND | DIODE SCHOTTKY 45V 10A | CFP15
3 | D10 D11 D12 D13 D14 D15 D16 D17 D18 D2 D3 D4 D5 D6 D7 D8 D9 | 17 | Lite-On Inc. | LTST-C170GKT | Digi-Key | 160-1179-1-ND | LED GREEN CLEAR SMD | 0805 (2012 Metric)
4 | HPS1 HPS2 HPS3 HPS4 | 4 | Infineon Technologies | BTS3256DAUMA1 | Digi-Key | BTS3256DAUMA1CT-ND | IC SWITCH SMART LOWSIDE | TO-252-5
5 | J1 J2 | 2 | Sullins Connector Solutions | PBC25SAAN | Digi-Key | S1011E-25-ND | CONN HEADER VERT 25POS 2.54MM
6 | J10 J11 J12 J5 J6 J7 J8 J9 | 8 | Phoenix Contact | 1411976 | Digi-Key | 277-10282-1-ND | CONN FMALE INSERT 5POS SOLDER
7 | J3 | 1 | HARTING | 09551156612741 | Digi-Key | 1195-4005-1-ND | CONN D-SUB RCPT 9POS SMD SOLDER
8 | J4 | 1 | HARTING | 09551296812741 | Digi-Key | 1195-4006-1-ND | CONN D-SUB PLUG 9POS SMD SOLDER
9 | P1 | 1 | Molex | 0039301060 | Digi-Key | WM1353-ND | CONN HEADER 6POS 4.2MM R/A TIN
10 | R1 | 1 | Panasonic Electronic Components | ERJ-6ENF2201V | Digi-Key | P2.20KCCT-ND | RES SMD 2.2K OHM 1% 1/8W | 0805 (2012 Metric)
11 | R10 R12 R14 R16 R18 R19 R2 R20 R21 R22 R23 R24 R25 R4 R6 R8 | 16 | Panasonic Electronic Components | ERJ-6ENF2870V | Digi-Key | P287CCT-ND | RES SMD 287 OHM 1% 1/8W | 0805 (2012 Metric)
12 | R11 R13 R15 R17 | 4 | Panasonic Electronic Components | ERJ-6ENF75R0V | Digi-Key | P75.0CCT-ND | RES SMD 75 OHM 1% 1/8W | 0805 (2012 Metric)
13 | R3 R5 R7 R9 | 4 | Panasonic Electronic Components | ERJ-6ENF5901V | Digi-Key | P5.90KCCT-ND | RES SMD 5.9K OHM 1% 1/8W | 0805 (2012 Metric)
14 | U1 U2 | 2 | Texas Instruments | SN74ABT541BDWR | Digi-Key | 296-14668-1-ND | Buffer Non-Inverting 1 Element 8 Bit per Element Push-Pull Output | 20-SOIC
15 | U10 U3 U4 U5 U6 U7 U8 U9 | 8 | ON Semiconductor | NUD3124LT1G | Digi-Key | NUD3124LT1GOSCT-ND | IC INDCT LOAD DRVR AUTO | SOT-23-3

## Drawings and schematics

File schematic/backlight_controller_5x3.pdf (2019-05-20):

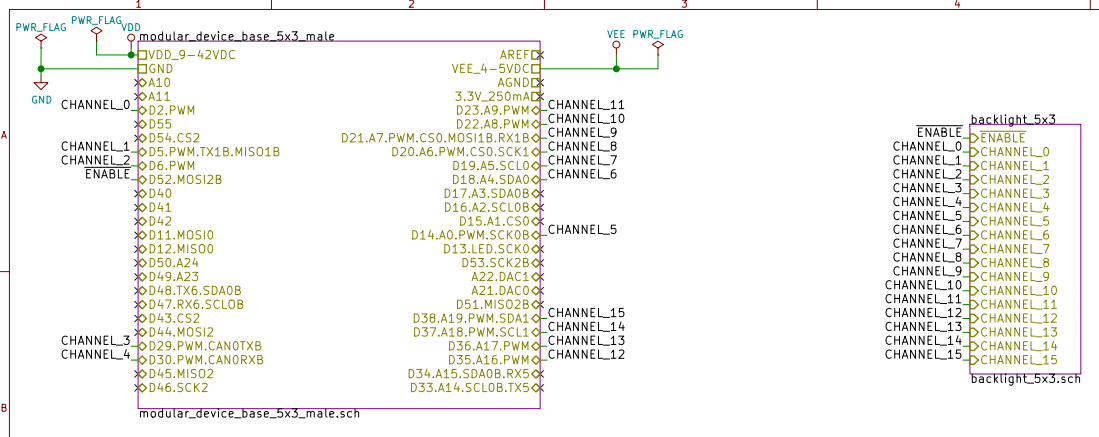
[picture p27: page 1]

File: backlight_controller_5x3.sch Sheet: / Janelia

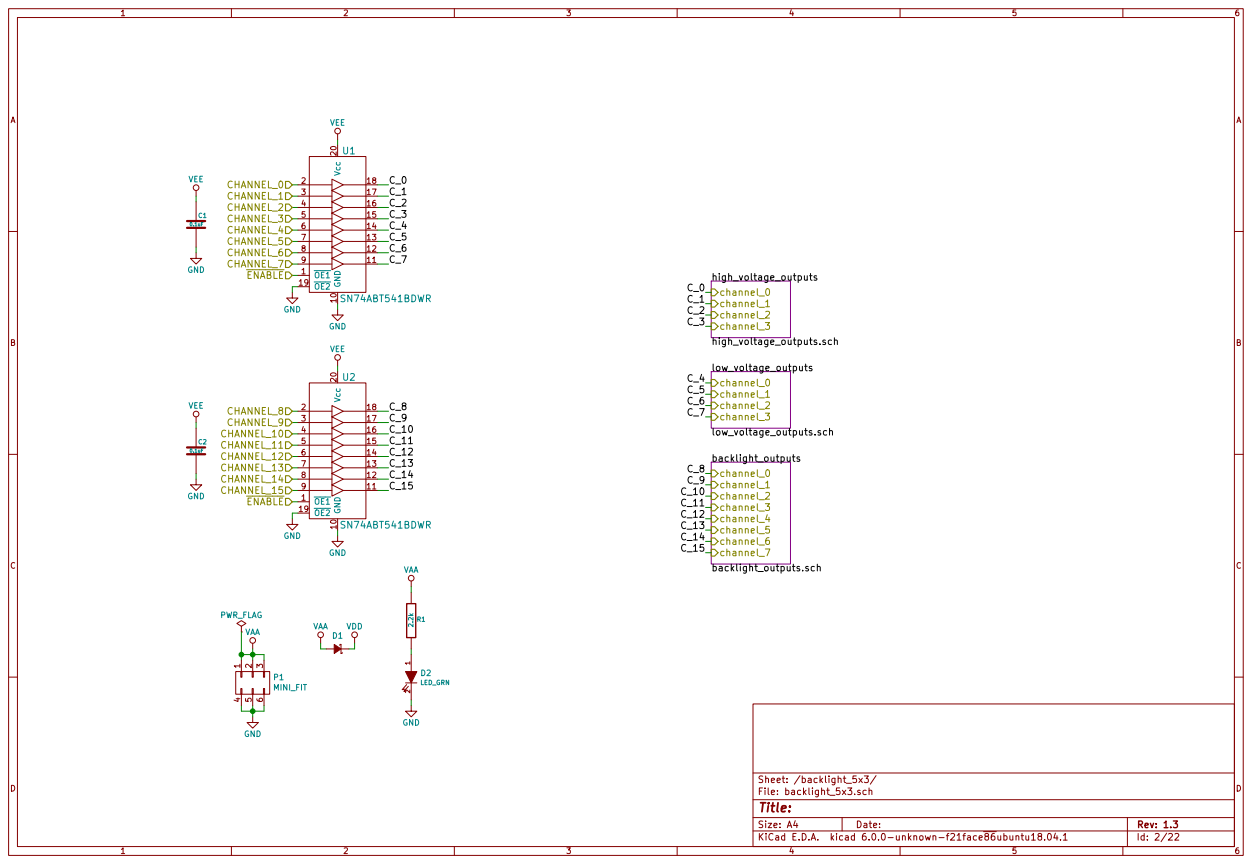
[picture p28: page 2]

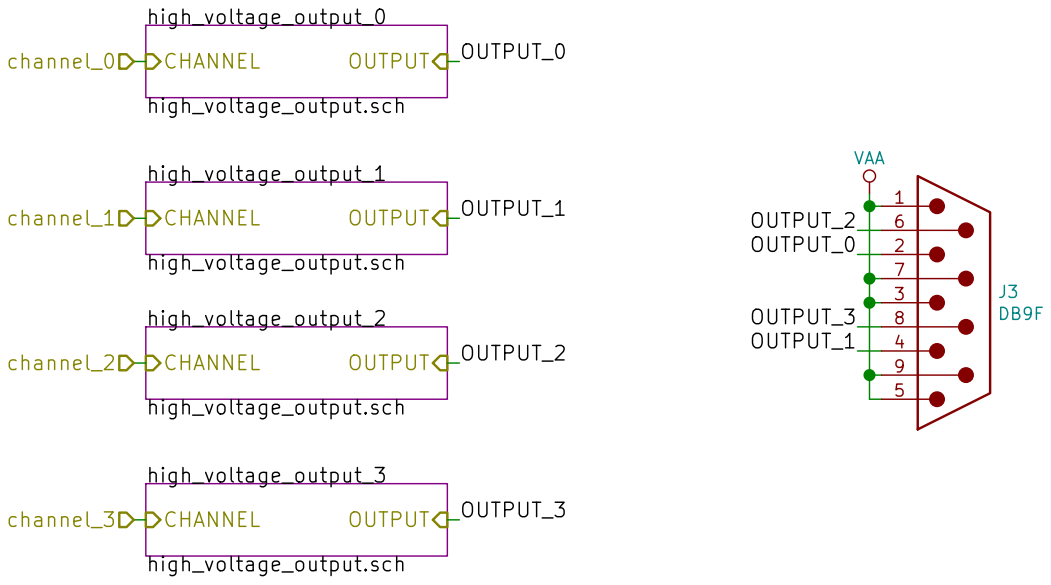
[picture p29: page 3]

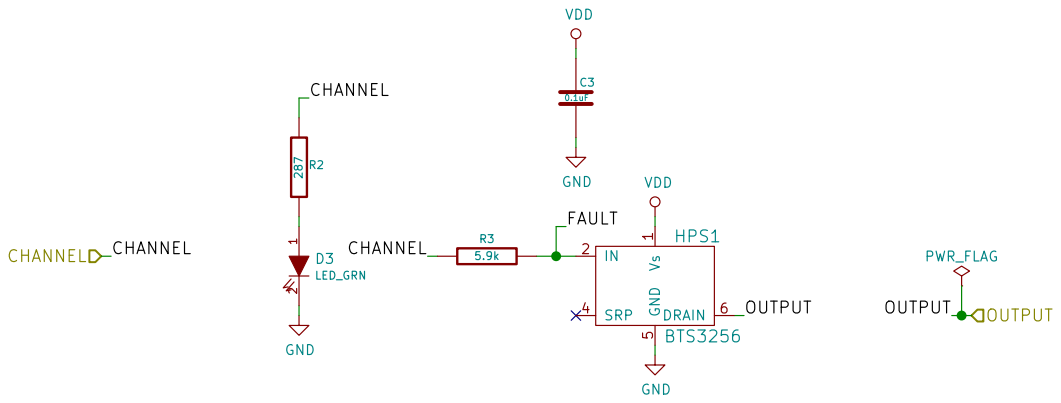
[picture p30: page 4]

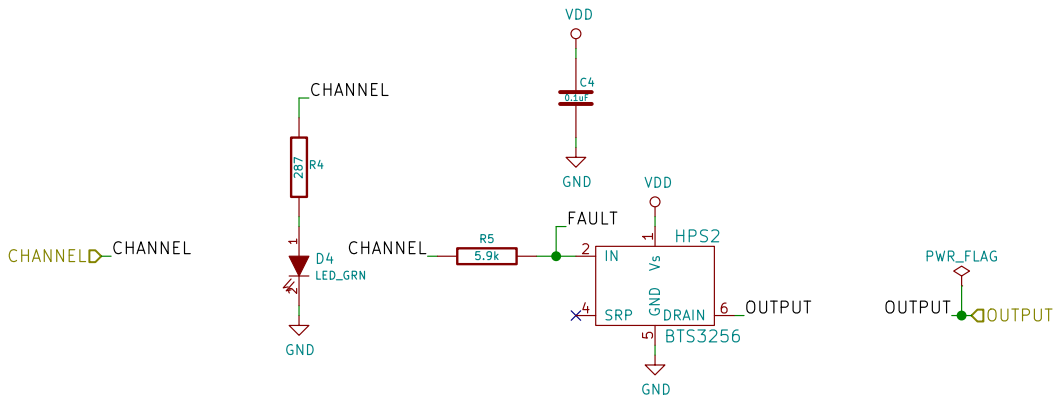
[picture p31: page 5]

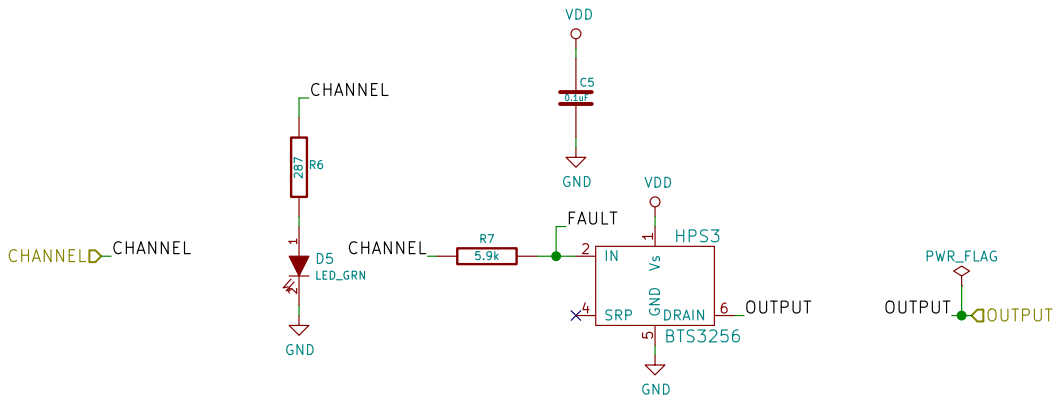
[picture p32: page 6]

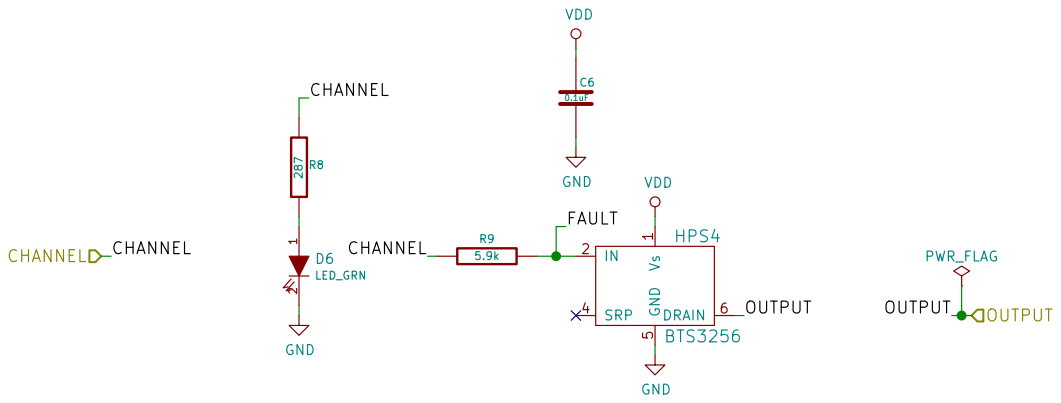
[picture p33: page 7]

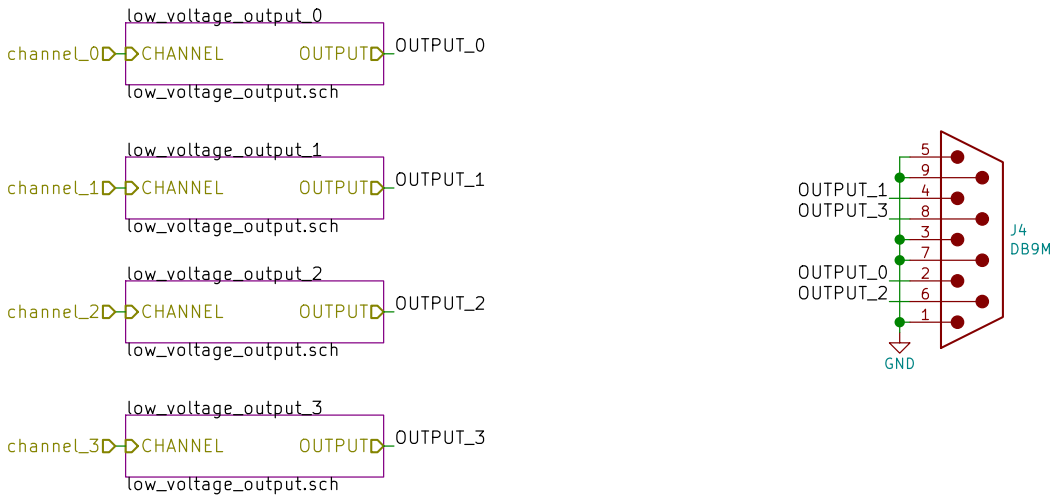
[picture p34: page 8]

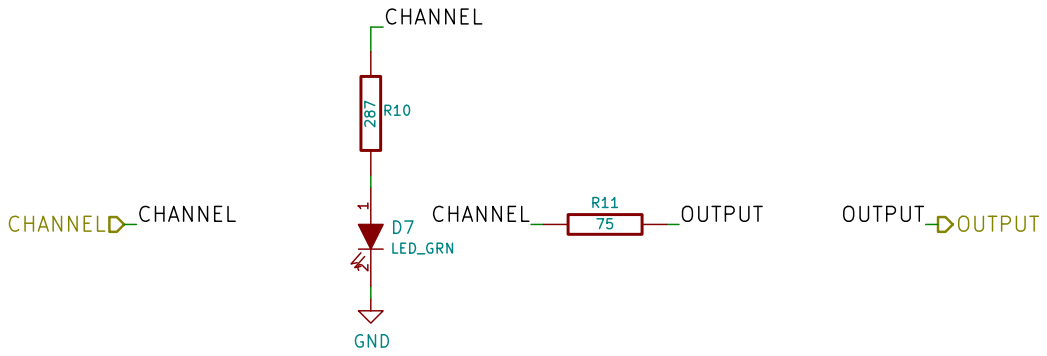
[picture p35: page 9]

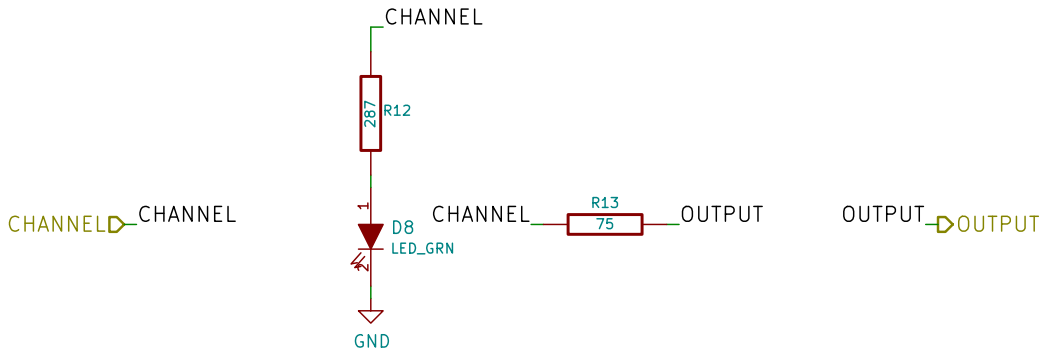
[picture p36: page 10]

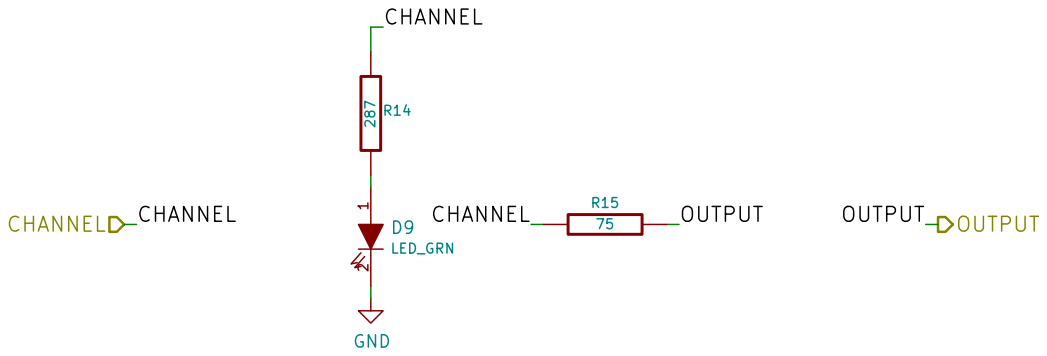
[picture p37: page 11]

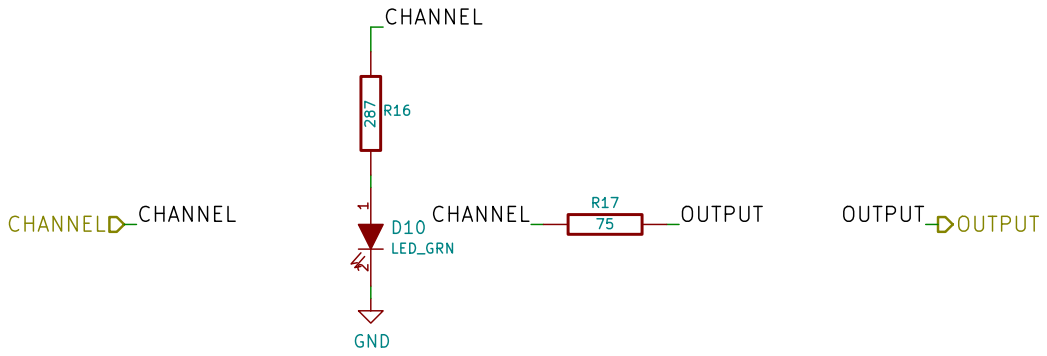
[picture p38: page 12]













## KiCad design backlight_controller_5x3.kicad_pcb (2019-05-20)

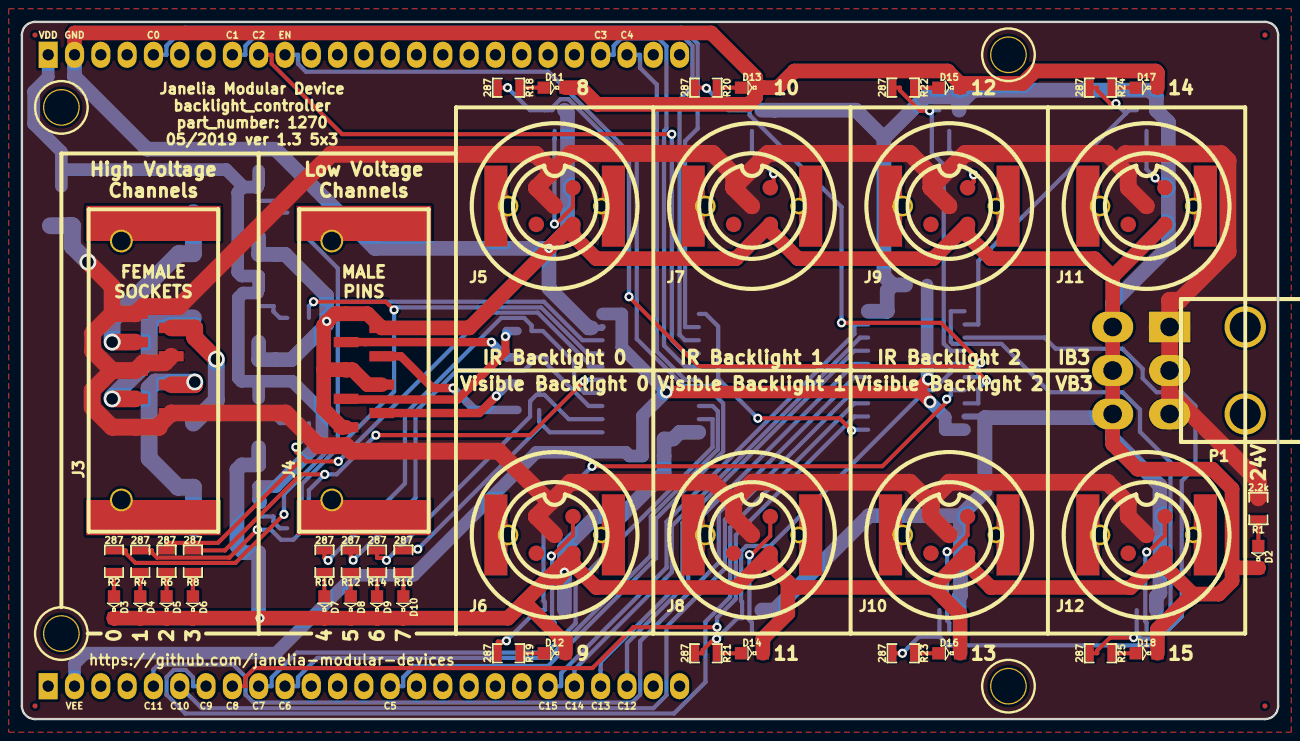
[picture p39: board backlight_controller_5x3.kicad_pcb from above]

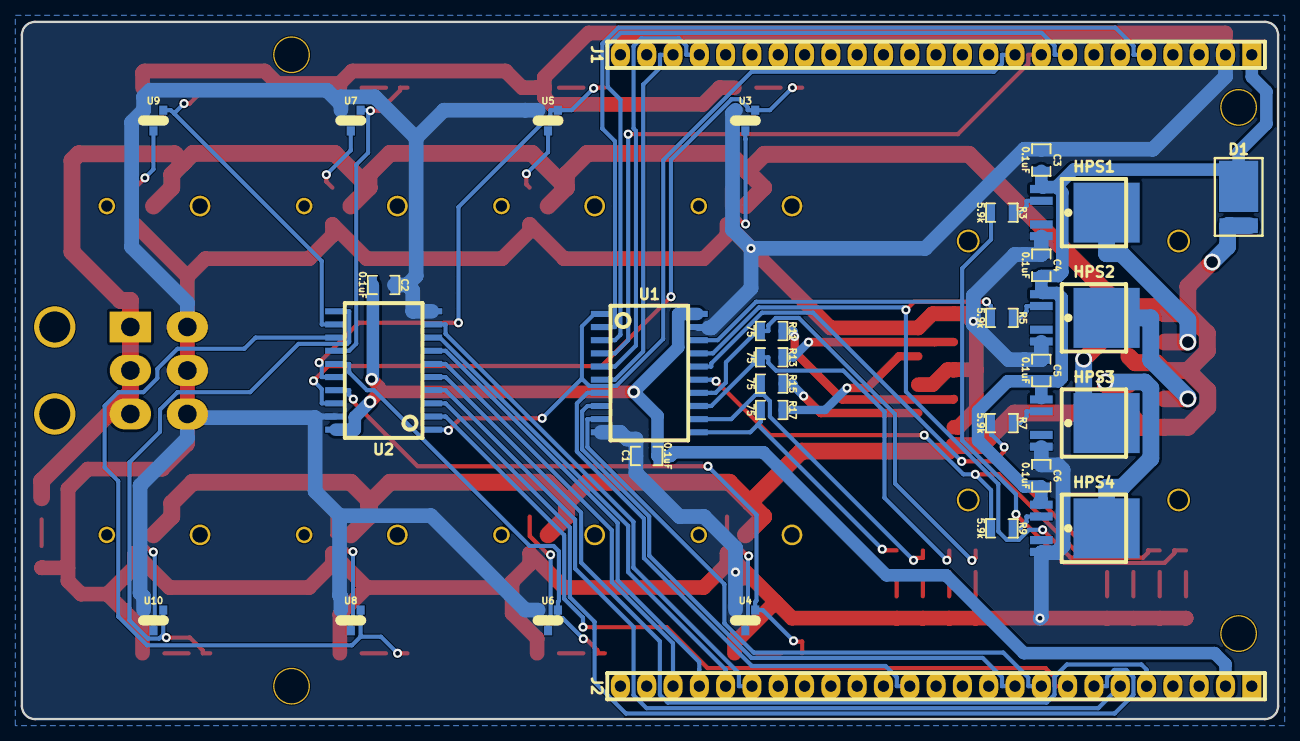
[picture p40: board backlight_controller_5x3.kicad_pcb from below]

Board: 2 copper layers, 121.3 x 67.3 mm, 84 parts (31 on the bottom side), 74 nets.

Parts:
C1, C2, C3, C4, C5, C6: 0.1uF; SM0805
D1: DIODE_10A; CFP15
D2, D3, D4, D5, D6, D7, D8, D9, D10, D11, D12, D13, D14, D15, D16, D17, D18: LED_GRN; LED0805
FID1, FID2, FID3, FID4: FIDUCIAL
HPS1, HPS2, HPS3, HPS4: BTS3256; PG-TO252-5-11
J1, J2: HEADER_01X25_MALE; HEADER_01x25
J3: DB9F; DB9F_SMD
J4: DB9M; DB9M_SMD
J5, J6, J7, J8, J9, J10, J11, J12: M12-5-RCPT; M12-5_RCPT_F_SMD
MH1, MH2, MH3, MH4: MOUNTING_HOLE_4-40
P1: MINI_FIT; MINI-FIT-JR_02X03_M_RA
R1: 2.2k; SM0805
R2, R4, R6, R8, R10, R12, R14, R16, R18, R19, R20, R21, R22, R23, R24, R25: 287; SM0805
R3, R5, R7, R9: 5.9k; SM0805
R11, R13, R15, R17: 75; SM0805
U1, U2: SN74ABT541BDWR; SOIC_20
U3, U4, U5, U6, U7, U8, U9, U10: NUD3124; TO-236-3

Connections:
/CHANNEL_0: J1.5, U1.2
/CHANNEL_1: J1.8, U1.3
/CHANNEL_2: J1.9, U1.4
/CHANNEL_3: J1.22, U1.5
/CHANNEL_4: J1.23, U1.6
/CHANNEL_5: J2.14, U1.7
/CHANNEL_6: J2.10, U1.8
/CHANNEL_7: J2.9, U1.9
/CHANNEL_8: J2.8, U2.2
/CHANNEL_9: J2.7, U2.3
/CHANNEL_10: J2.6, U2.4
/CHANNEL_11: J2.5, U2.5
/CHANNEL_12: J2.23, U2.6
/CHANNEL_13: J2.22, U2.7
/CHANNEL_14: J2.21, U2.8
/CHANNEL_15: J2.20, U2.9
/backlight_5x3/C_0: R2.1, R3.1, U1.18
/backlight_5x3/C_1: R4.1, R5.1, U1.17
/backlight_5x3/C_2: R6.1, R7.1, U1.16
/backlight_5x3/C_3: R8.1, R9.1, U1.15
/backlight_5x3/C_4: R10.1, R11.1, U1.14
/backlight_5x3/C_5: R12.1, R13.1, U1.13
/backlight_5x3/C_6: R14.1, R15.1, U1.12
/backlight_5x3/C_7: R16.1, R17.1, U1.11
/backlight_5x3/C_8: R18.1, U2.18, U3.1
/backlight_5x3/C_9: R19.1, U2.17, U4.1
/backlight_5x3/C_10: R20.1, U2.16, U5.1
/backlight_5x3/C_11: R21.1, U2.15, U6.1
/backlight_5x3/C_12: R22.1, U2.14, U7.1
/backlight_5x3/C_13: R23.1, U2.13, U8.1
/backlight_5x3/C_14: R24.1, U2.12, U9.1
/backlight_5x3/C_15: R25.1, U2.11, U10.1
/backlight_5x3/backlight_outputs/ir_0/NPN: J5.2, U3.3
/backlight_5x3/backlight_outputs/ir_1/NPN: J7.2, U5.3
/backlight_5x3/backlight_outputs/ir_2/NPN: J9.2, U7.3
/backlight_5x3/backlight_outputs/ir_3/NPN: J11.2, U9.3
/backlight_5x3/backlight_outputs/visible_0/NPN: J6.2, U4.3
/backlight_5x3/backlight_outputs/visible_1/NPN: J8.2, U6.3
/backlight_5x3/backlight_outputs/visible_2/NPN: J10.2, U8.3
/backlight_5x3/backlight_outputs/visible_3/NPN: J12.2, U10.3
/backlight_5x3/high_voltage_outputs/OUTPUT_0: HPS1.6, J3.2
/backlight_5x3/high_voltage_outputs/OUTPUT_1: HPS2.6, J3.4
/backlight_5x3/high_voltage_outputs/OUTPUT_2: HPS3.6, J3.6
/backlight_5x3/high_voltage_outputs/OUTPUT_3: HPS4.6, J3.8
/backlight_5x3/high_voltage_outputs/high_voltage_output_0/FAULT: HPS1.2, R3.2
/backlight_5x3/high_voltage_outputs/high_voltage_output_1/FAULT: HPS2.2, R5.2
/backlight_5x3/high_voltage_outputs/high_voltage_output_2/FAULT: HPS3.2, R7.2
/backlight_5x3/high_voltage_outputs/high_voltage_output_3/FAULT: HPS4.2, R9.2
/backlight_5x3/low_voltage_outputs/OUTPUT_0: J4.2, R11.2
/backlight_5x3/low_voltage_outputs/OUTPUT_1: J4.4, R13.2
/backlight_5x3/low_voltage_outputs/OUTPUT_2: J4.6, R15.2
/backlight_5x3/low_voltage_outputs/OUTPUT_3: J4.8, R17.2
/~ENABLE: J1.10, U1.1, U2.1
GND: C1.2, C2.2, C3.2, C4.2, C5.2, C6.2, D2.2, D3.2, D4.2, D5.2, D6.2, D7.2, D8.2, D9.2, D10.2, D11.2, D12.2, D13.2, D14.2, D15.2, D16.2, D17.2, D18.2, HPS1.5, HPS2.5, HPS3.5, HPS4.5, J1.2, J4.1, J4.3, J4.5, J4.7, J4.9, J5.3, J6.3, J7.3, J8.3, J9.3, J10.3, J11.3, J12.3, P1.4, P1.5, P1.6, U1.10, U1.19, U2.10, U2.19, U3.2, U4.2, U5.2, U6.2, U7.2, U8.2, U9.2, U10.2
unnamed: D2.1, R1.2
unnamed: D3.1, R2.2
unnamed: D4.1, R4.2
unnamed: D5.1, R6.2
unnamed: D6.1, R8.2
unnamed: D7.1, R10.2
unnamed: D8.1, R12.2
unnamed: D9.1, R14.2
unnamed: D10.1, R16.2
unnamed: D11.1, R18.2
unnamed: D12.1, R19.2
unnamed: D13.1, R20.2
unnamed: D14.1, R21.2
unnamed: D15.1, R22.2
unnamed: D16.1, R23.2
unnamed: D17.1, R24.2
unnamed: D18.1, R25.2
VAA: D1.2, J3.1, J3.3, J3.5, J3.7, J3.9, J5.1, J5.5, J6.1, J6.5, J7.1, J7.5, J8.1, J8.5, J9.1, J9.5, J10.1, J10.5, J11.1, J11.5, J12.1, J12.5, P1.1, P1.2, P1.3, R1.1
VDD: C3.1, C4.1, C5.1, C6.1, D1.1, HPS1.1, HPS2.1, HPS3.1, HPS4.1, J1.1
VEE: C1.1, C2.1, J2.2, U1.20, U2.20

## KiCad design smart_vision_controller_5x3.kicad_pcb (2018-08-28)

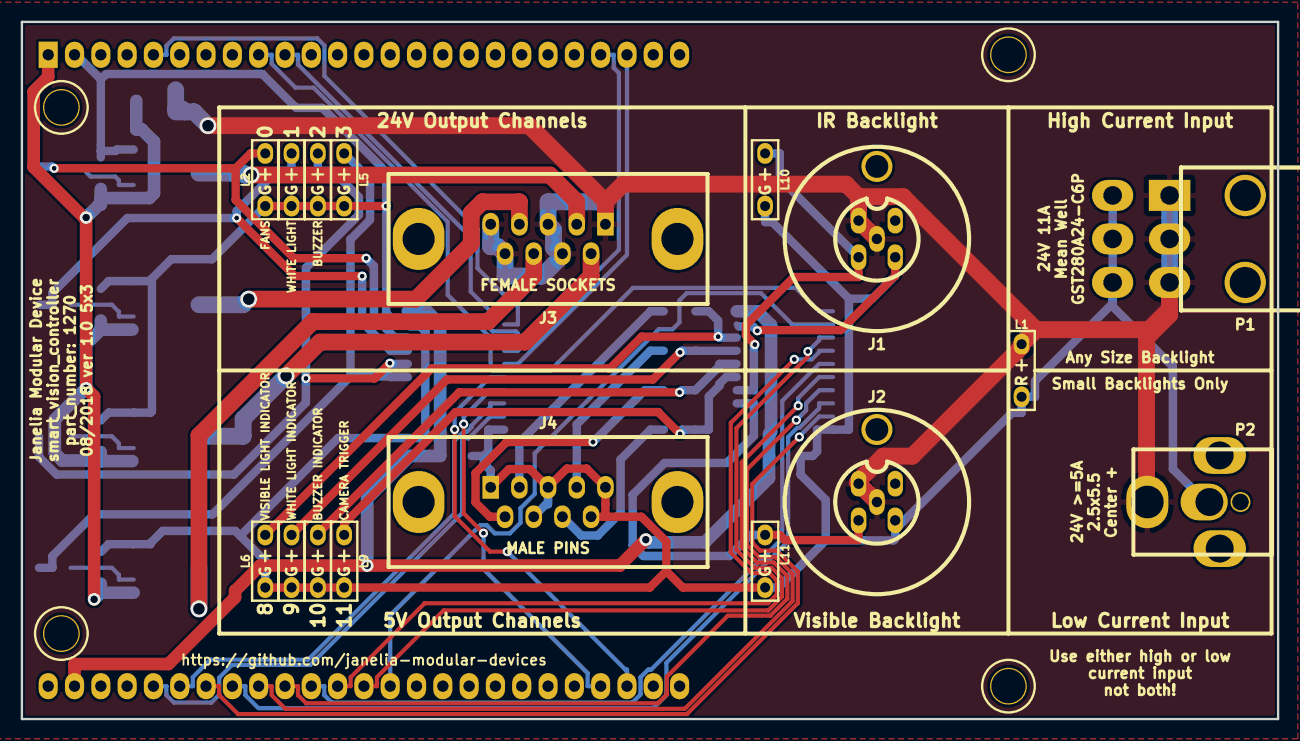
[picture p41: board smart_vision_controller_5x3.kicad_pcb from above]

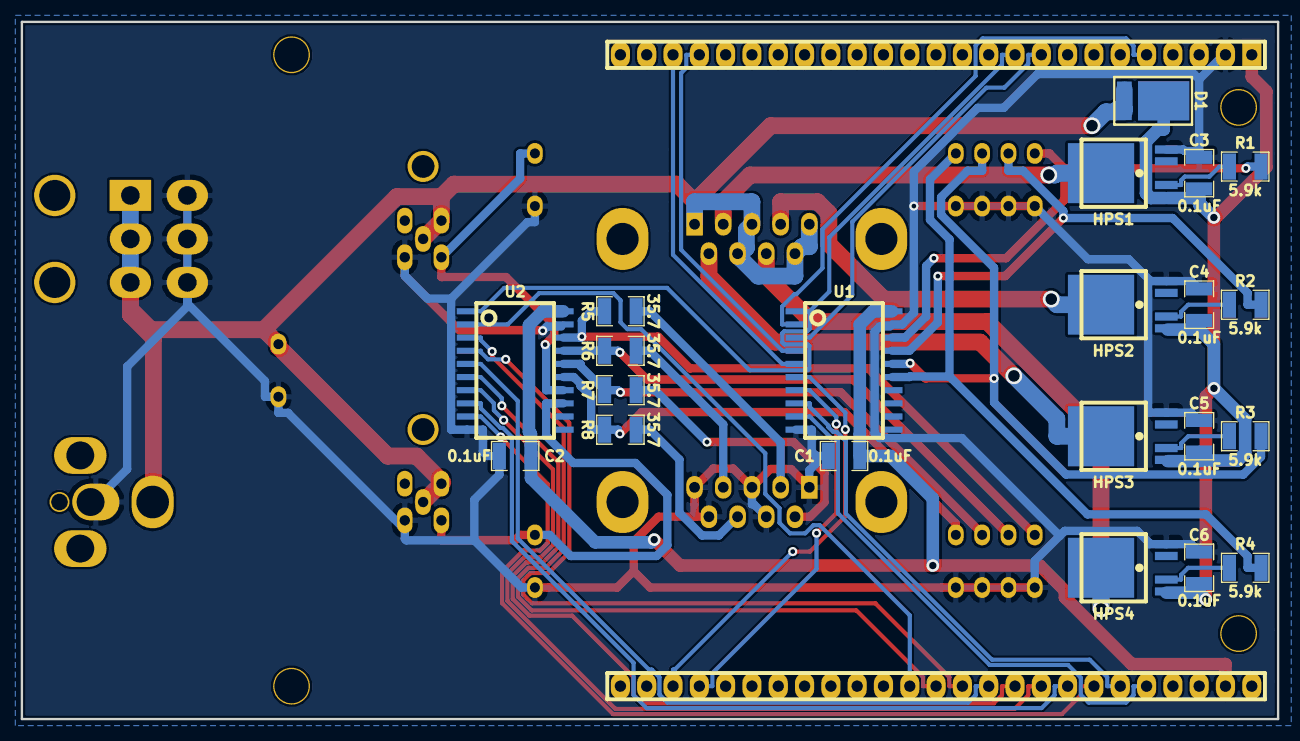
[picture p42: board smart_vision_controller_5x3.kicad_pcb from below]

Board: 2 copper layers, 121.3 x 67.3 mm, 39 parts (21 on the bottom side), 43 nets.

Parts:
C1, C2, C3, C4, C5, C6: 0.1uF; SM1210
D1: diode_schottky_45V_10A; CFP15
HPS1, HPS2, HPS3, HPS4: BTS3256; PG-TO252-5-11
J1, J2: M12-5_RCPT_F
J3: DB9F
J4: DB9M
L1: LED_24V_RED; LED_555-3XXX_R
L2, L3, L4, L5, L6, L7, L8, L9, L10, L11: LED_5V_GRN; LED_555-3XXX_G
MDB1: MODULAR_DEVICE_BASE_5x3_MALE; MODULAR_DEVICE_BASE_5X3_MALE
P1: MINI_FIT_JR_02X03_M_RA; MINI-FIT-JR_02X03_M_RA
P2: PWR_JACK_2.5x5.5; DCJACK_2PIN_HIGHCURRENT
R1, R2, R3, R4: 5.9k; SM1210
R5, R6, R7, R8: 35.7; SM1210
U1, U2: SN74ABT541BDWR; SOIC_20

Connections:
/BUZZER: HPS3.6, J3.6
/BUZZER_INDICATOR: J4.6, R7.1
/CAMERA_TRIGGER: J4.8, R8.1
/CHANNEL_0: MDB1.2, U1.2
/CHANNEL_1: MDB1.6, U1.3
/CHANNEL_2: MDB1.29, U1.4
/CHANNEL_3: MDB1.30, U1.5
/CHANNEL_4: MDB1.35, U1.6
/CHANNEL_5: MDB1.36, U1.7
/CHANNEL_6: MDB1.22, U1.8
/CHANNEL_7: MDB1.23, U1.9
/CHANNEL_8: MDB1.14, U2.2
/CHANNEL_9: MDB1.15, U2.3
/CHANNEL_10: MDB1.16, U2.4
/CHANNEL_11: MDB1.17, U2.5
/CHANNEL_12: MDB1.18, U2.6
/CHANNEL_13: MDB1.19, U2.7
/CHANNEL_14: MDB1.20, U2.8
/CHANNEL_15: MDB1.21, U2.9
/C_0: L2.1, R1.2, U1.18
/C_1: L3.1, R2.2, U1.17
/C_2: L4.1, R3.2, U1.16
/C_3: L5.1, R4.2, U1.15
/C_8: L6.1, R5.2, U2.18
/C_9: L7.1, R6.2, U2.17
/C_10: L8.1, R7.2, U2.16
/C_11: L9.1, R8.2, U2.15
/C_12: J1.4, L10.1, U2.14
/C_13: J2.4, L11.1, U2.13
/FANS: HPS1.6, J3.2
/OUTPUT_3: HPS4.6, J3.8
/VISIBLE_LIGHT_INDICATOR: J4.2, R5.1
/WHITE_LIGHT: HPS2.6, J3.4
/WHITE_LIGHT_INDICATOR: J4.4, R6.1
/output_0/FAULT: HPS1.2, R1.1
/output_1/FAULT: HPS2.2, R2.1
/output_2/FAULT: HPS3.2, R3.1
/output_3/FAULT: HPS4.2, R4.1
/~ENABLE: MDB1.52, U1.1, U2.1
GND: C1.2, C2.2, C3.2, C4.2, C5.2, C6.2, HPS1.5, HPS2.5, HPS3.5, HPS4.5, J1.3, J2.3, J4.1, J4.3, J4.5, J4.7, J4.9, L1.2, L2.2, L3.2, L4.2, L5.2, L6.2, L7.2, L8.2, L9.2, L10.2, L11.2, MDB1.GND, P1.4, P1.5, P1.6, P2.2, U1.10, U1.19, U2.10, U2.19
VAA: D1.2, J1.1, J1.5, J2.1, J2.5, J3.1, J3.3, J3.5, J3.7, J3.9, L1.1, P1.1, P1.2, P1.3, P2.1
VDD: C3.1, C4.1, C5.1, C6.1, D1.1, HPS1.1, HPS2.1, HPS3.1, HPS4.1, MDB1.VDD
VEE: C1.1, C2.1, MDB1.VEE, U1.20, U2.20

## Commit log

2018-08-09 Initial commit.
    [smart_vision_controller_5x3-B.Cu.gbl, smart_vision_controller_5x3-B.Mask.gbs, smart_vision_controller_5x3-B.SilkS.gbo, smart_vision_controller_5x3-F.Cu.gtl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]
2018-08-09 Added some components and footprints.
    [smart_vision_controller_5x3.kicad_pcb]
2018-08-09 Added DB-9 components.
    [smart_vision_controller_5x3.sch]
2018-08-10 Added more parts and partially filled out bom.
    [smart_vision_controller_5x3.sch, supplemental_digikey_parts.csv]
2018-08-23 Partially designed.
    [high_power_channel.sch, low_power_channel.sch, smart_vision_controller_5x3.sch, supplemental_digikey_parts.csv]
2018-08-23 Added digikey_order.
    [digikey_order.csv]
2018-08-23 Added items.
    [digikey_order.csv]
2018-08-23 Added low_power_channels.
    [high_power_channel.sch, low_power_channel.sch, smart_vision_controller_5x3.sch, supplemental_digikey_parts.csv]
2018-08-24 Removed F.SilkS from pads.
    [high_power_channel.sch, low_power_channel.sch, smart_vision_controller_5x3.kicad_pcb, smart_vision_controller_5x3.sch]
2018-08-24 Finished layout of v1.0.
    [digikey_order.csv, smart_vision_controller_5x3.dsn, smart_vision_controller_5x3.kicad_pcb, smart_vision_controller_5x3.sch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]
2018-08-27 Finished version 1.0.
    [smart_vision_controller_5x3-B.Cu.gbl, smart_vision_controller_5x3-B.Mask.gbs, smart_vision_controller_5x3-B.SilkS.gbo, smart_vision_controller_5x3-F.Cu.gtl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]
2018-08-27 Added some documentation.
    [digikey_parts.csv]
2018-08-27 Removed *.SilkS from pads.
    [digikey_order.csv]
2018-08-27 Added 24V led and swapped green led for one in stock.
    [high_power_channel.sch, low_power_channel.sch, smart_vision_controller_5x3.kicad_pcb, smart_vision_controller_5x3.sch]
2018-08-27 Switched back to smaller leds.
    [backlight_channel.sch, high_power_channel.sch, low_power_channel.sch, smart_vision_controller_5x3.kicad_pcb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]
2018-08-28 Rerouted traces.
    [backlight_output.sch, digikey_order.csv, high_power_output.sch, low_power_output.sch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]
2018-08-28 Added to supplemental bom.
    [digikey_order.csv, digikey_parts.csv, smart_vision_controller_5x3-B.Cu.gbl, smart_vision_controller_5x3-B.Mask.gbs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]
2018-09-10 smart_vision -> sleep_rig.
    [backlight_output.sch, high_power_output.sch, low_power_output.sch, sleep_rig_controller_5x3-B.Cu.gbl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]
2018-09-10 Rearranged components.
    [backlight_output.sch, high_power_output.sch, low_power_output.sch, sleep_rig_controller_5x3.kicad_pcb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]
2018-09-11 More progress towards v1.0.
    [backlight_output.sch, high_power_output.sch, low_power_output.sch, sleep_rig_controller_5x3.sch]
2018-09-12 sleep_rig -> backlight.
    [backlight_controller_5x3-B.Cu.gbl, backlight_controller_5x3-B.Mask.gbs, backlight_controller_5x3-B.SilkS.gbo, backlight_controller_5x3-F.Cu.gtl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]
2018-09-12 Reorganized schematics.
    [backlight_controller_5x3.kicad_pcb, backlight_controller_5x3.sch, backlight_output.sch, backlight_outputs.sch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]
2018-09-12 Finished schematic v1.0.
    [backlight_controller_5x3.sch, backlight_output.sch, backlight_outputs.sch, high_power_output.sch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]
2018-09-12 Initial footprint layout.
    [backlight_controller_5x3.kicad_pcb, backlight_output.sch, high_power_output.sch, high_power_outputs.sch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]
2018-09-12 Another schematic reorganization.
    [backlight_5x3.sch, backlight_controller_5x3-B.Cu.gbl, backlight_controller_5x3-B.Mask.gbs, backlight_controller_5x3-B.SilkS.gbo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]
2018-09-12 Reorganized schematics, ready to layout traces.
    [backlight_5x3.sch, backlight_controller_5x3.dsn, backlight_controller_5x3.kicad_pcb, backlight_controller_5x3.sch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]
2018-09-12 Added autorouted traces.
    [backlight_controller_5x3.kicad_pcb]
2018-09-13 Updated documentation.
    [digikey_order.csv, digikey_parts.csv, supplemental_digikey_parts.csv]
2018-10-19 Changes towards v1.1.
    [backlight_5x3.sch, backlight_controller_5x3.kicad_pcb, backlight_controller_5x3.sch, backlight_output.sch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]
2018-10-20 Finished version 1.1.
    [backlight_5x3.sch, backlight_controller_5x3-B.Cu.gbl, backlight_controller_5x3-B.Mask.gbs, backlight_controller_5x3-B.SilkS.gbo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]
2018-10-23 Updated version 1.1 documentation.
    [digikey_order.csv, supplemental_digikey_parts.csv]
2018-10-26 Updated supplemental bom.
    [supplemental_digikey_parts.csv]
2018-10-29 high_power -> high_voltage. low_power -> low_voltage.
    [backlight_5x3.sch, backlight_controller_5x3-B.Cu.gbl, backlight_controller_5x3-F.Cu.gtl, backlight_controller_5x3.dsn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]
2018-10-29 Progress towards v1.2.
    [backlight_5x3.sch, backlight_controller_5x3.kicad_pcb, backlight_controller_5x3.sch, backlight_output.sch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]
2018-10-29 Finished v1.2 schematic.
    [backlight_controller_5x3.kicad_pcb, backlight_output.sch, low_voltage_output.sch]
2018-10-29 Finished version 1.2.
    [backlight_controller_5x3-B.Cu.gbl, backlight_controller_5x3-B.Mask.gbs, backlight_controller_5x3-B.SilkS.gbo, backlight_controller_5x3-F.Cu.gtl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]
2019-05-09 Prepare for version 1.3
    [backlight_controller_5x3.kicad_pcb]
2019-05-09 Remove old components
    [backlight_5x3.sch, backlight_controller_5x3.sch, backlight_output.sch, backlight_outputs.sch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]
2019-05-09 Add modular_device_base_5x3_male
    [backlight_controller_5x3.sch, modular_device_base_5x3_male.sch]
2019-05-13 Make modular device base schematic
    [backlight_5x3.sch, backlight_controller_5x3.sch, backlight_output.sch, backlight_outputs.sch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]
2019-05-13 Finish schematic v1.3
    [backlight_5x3.sch, backlight_controller_5x3.sch, backlight_output.sch, high_voltage_output.sch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]
2019-05-17 Update schematic
    [backlight_controller_5x3.sch]
2019-05-17 Place footprints
    [backlight_controller_5x3.kicad_pcb, backlight_controller_5x3.sch, modular_device_base_5x3_male.sch]
2019-05-17 Update documentation
    [backlight_controller_5x3-B.Cu.gbl, backlight_controller_5x3-B.Mask.gbs, backlight_controller_5x3-B.SilkS.gbo, backlight_controller_5x3-B_Cu.gbl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]
2019-05-20 Fix missing component field values
    [backlight_controller_5x3-B_Cu.gbl, backlight_controller_5x3-B_Mask.gbs, backlight_controller_5x3-B_Paste.gbp, backlight_controller_5x3-B_SilkS.gbo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]
2019-05-20 Updated documentation
    [Digi-Key_parts.csv, bom.csv, digikey_order.csv, digikey_parts.csv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]
2021-09-21 Remove ignored files
    [backlight_controller_5x3.dsn]
